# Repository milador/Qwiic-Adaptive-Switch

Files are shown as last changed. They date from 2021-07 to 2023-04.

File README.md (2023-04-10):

# Qwiic-Adaptive-Switch

Qwiic-Adaptive-Switch modules provide an easy way to create your own adaptive switch input or output boxes through Qwiic or STEMMA QT ecosystem. Qwiic Adaptive Switch modules can be connected to any Qwiic enabled board to create an adaptive switch box.

You can find more information about <a href="https://www.sparkfun.com/qwiic">Qwiic Connect System</a> at SparkFun official website.

Qwiic-Adaptive-Switch modules use Qwiic/JST-SH-4Pin connector and IC2 interface to communicate with main microcontroller which means you can connect multiple switch modules by daisy chaining them. It's using TCA9534 bus expander.

## Qwiic-Adaptive-Switch-Input

Top View: 
<p align="center">
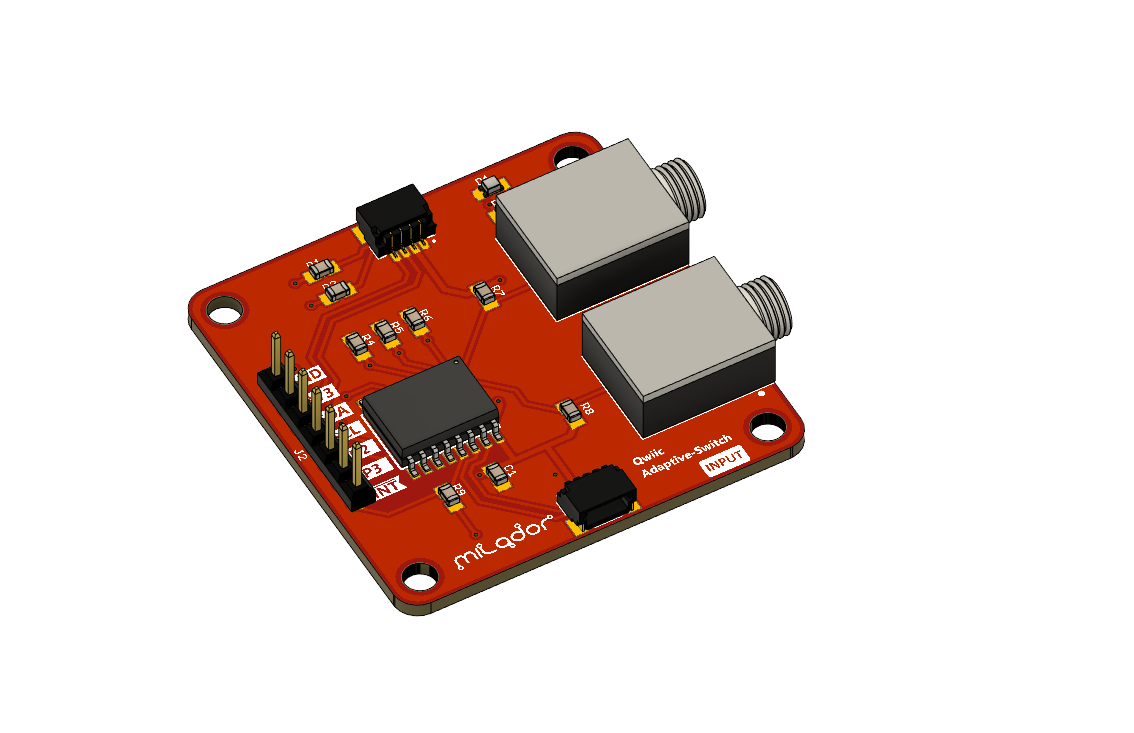
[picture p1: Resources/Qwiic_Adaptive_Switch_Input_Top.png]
Qwiic Adaptive Switch Input Top

</p>

Bottom View:
<p align="center">
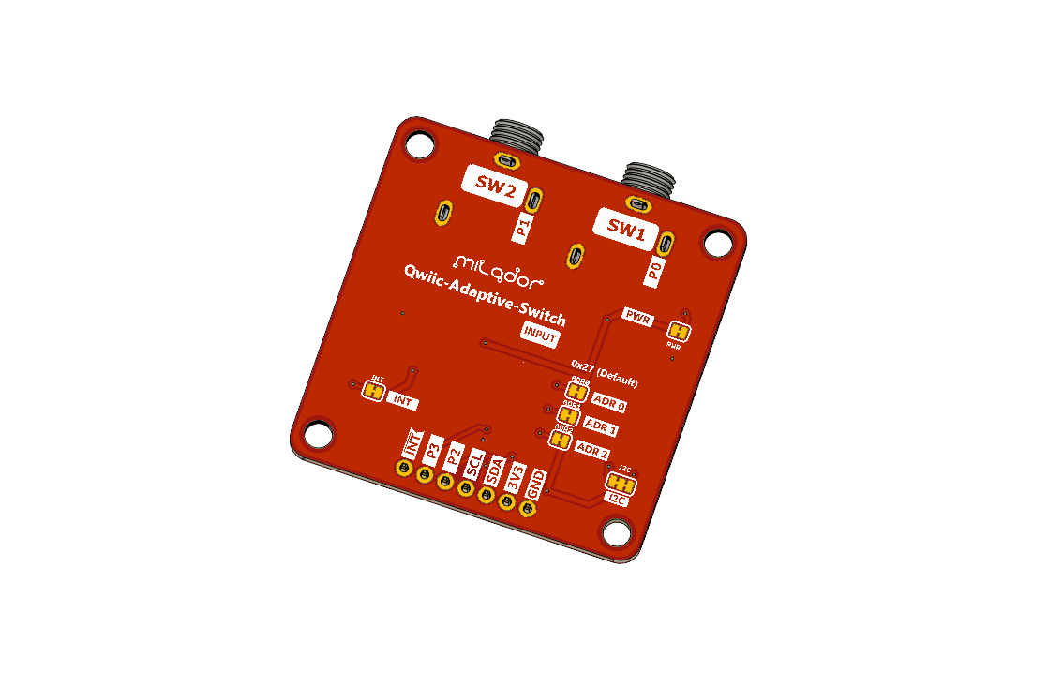
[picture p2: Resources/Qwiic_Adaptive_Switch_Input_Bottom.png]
Qwiic Adaptive Switch Input Bottom

</p>

## Qwiic-Adaptive-Switch-Output

Top View: 
<p align="center">
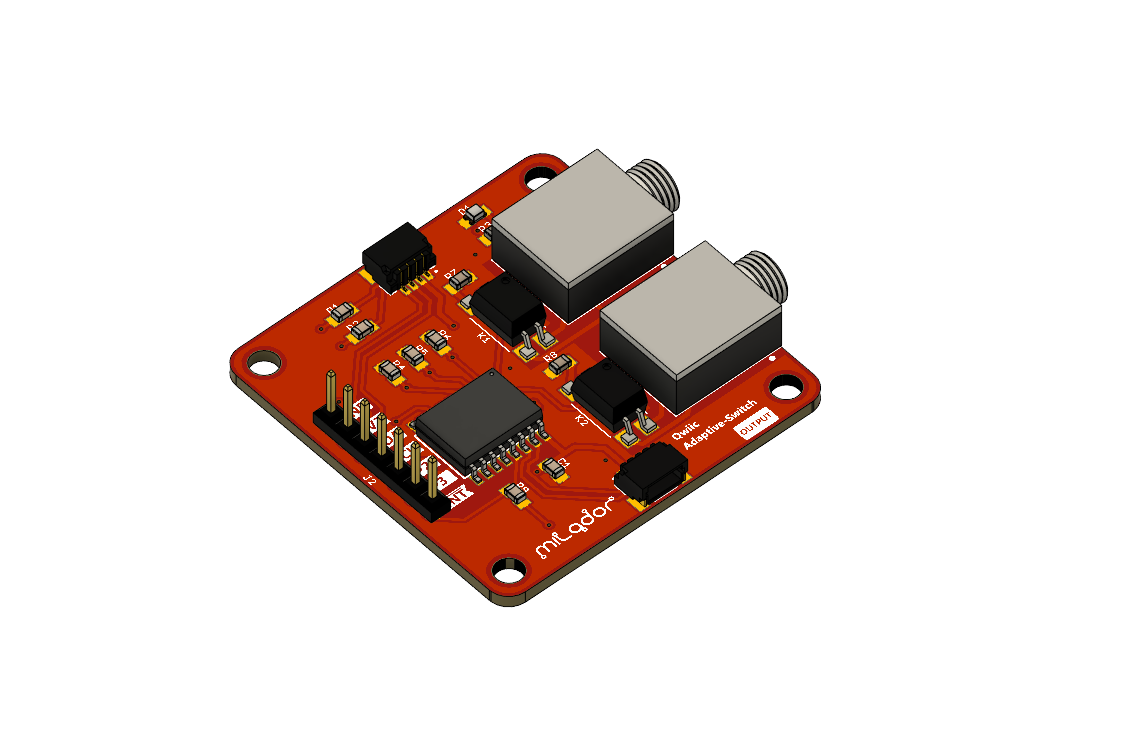
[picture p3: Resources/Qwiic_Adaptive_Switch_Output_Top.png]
Qwiic Adaptive Switch Output Top

</p>

Bottom View:
<p align="center">
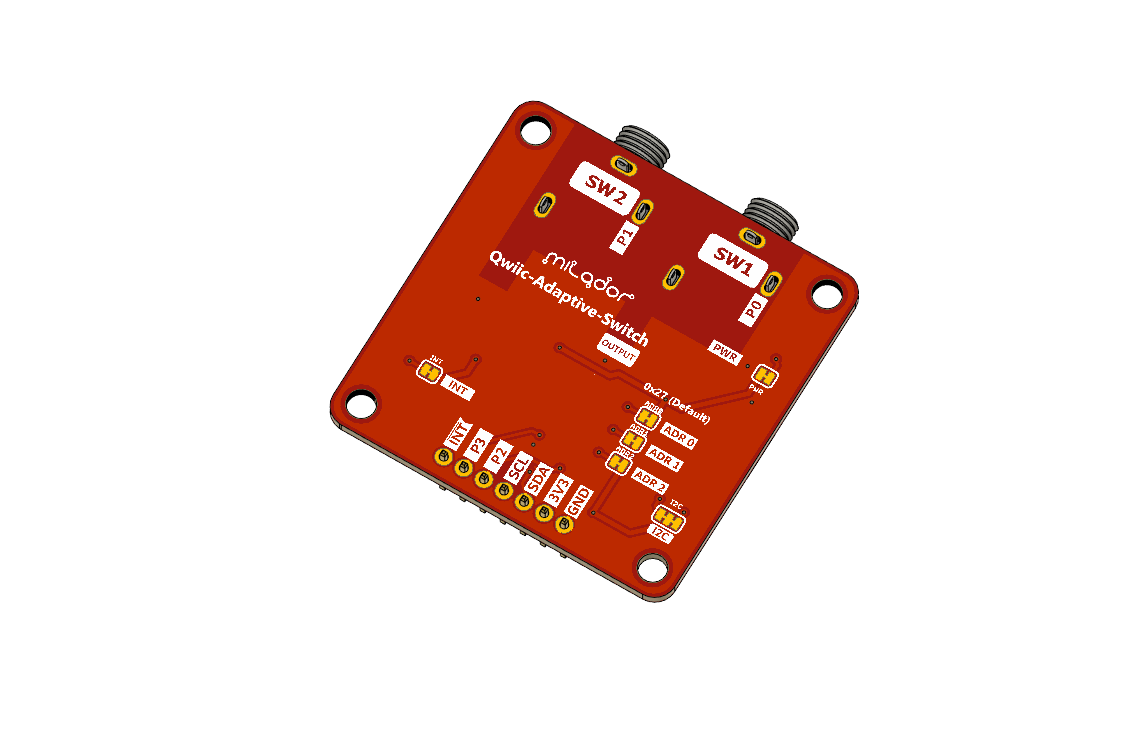
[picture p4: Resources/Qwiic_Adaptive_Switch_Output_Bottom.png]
Qwiic Adaptive Switch Output Bottom

</p>

## Risk Assessment

The Risk Assessment documents are located under [Documents](./Documents/) directory. 

## License

### MIT License

Copyright (c) 2021 milador

Permission is hereby granted, free of charge, to any person obtaining a copy of this software and associated documentation files (the "Software"), to deal in the Software without restriction, including without limitation the rights to use, copy, modify, merge, publish, distribute, sublicense, and/or sell copies of the Software, and to permit persons to whom the Software is furnished to do so, subject to the following conditions:

The above copyright notice and this permission notice shall be included in all copies or substantial portions of the Software.

THE SOFTWARE IS PROVIDED "AS IS", WITHOUT WARRANTY OF ANY KIND, EXPRESS OR IMPLIED, INCLUDING BUT NOT LIMITED TO THE WARRANTIES OF MERCHANTABILITY, FITNESS FOR A PARTICULAR PURPOSE AND NONINFRINGEMENT. IN NO EVENT SHALL THE AUTHORS OR COPYRIGHT HOLDERS BE LIABLE FOR ANY CLAIM, DAMAGES OR OTHER LIABILITY, WHETHER IN AN ACTION OF CONTRACT, TORT OR OTHERWISE, ARISING FROM, OUT OF OR IN CONNECTION WITH THE SOFTWARE OR THE USE OR OTHER DEALINGS IN THE SOFTWARE.

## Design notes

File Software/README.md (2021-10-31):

# Qwiic-Adaptive-Switch

## Software 

Qwiic-Adaptive-Switch-Input and Qwiic-Adaptive-Switch-Output modules both use TCA9534 bus expander to read or write status of switches. The TCA9534 bus expander converts GPIO to I2C data and you can use the existing I2C TCA9534 libraries to help you get started.

## Library 

### Arduino Library
You have two options if you are planning to use C++ and Arduino to write your code.

  1. [SparkFun_Qwiic_GPIO_Library](https://github.com/sparkfun/SparkFun_Qwiic_GPIO_Library) ( TCA9534 library created by SparkFun to be used with Qwiic Bus-Expander module )
  2. [TCA9534 library](https://github.com/hideakitai/TCA9534) ( TCA9534 library created by hideakitai )

### CircuitPython Library
You have the option to use the <a href="https://github.com/milador/Community_CircuitPython_TCA9534">Community_CircuitPython_TCA9534</a> library if you are planning to write your code in CircuitPython. 

## Example Code 

### Qwiic-Adaptive-Switch-Input Example Code

There is an example available to help you get started with Qwiic-Adaptive-Switch-Input module and SparkFun TCA9534 library. The <a href="https://raw.githubusercontent.com/milador/Qwiic-Adaptive-Switch/main/Software/Arduino/Qwiic_Adaptive_Switch_Input/Qwiic_Adaptive_Switch_Input.ino">Qwiic_Adaptive_Switch_Input.ino</a> example is available for testing purposes.

### Qwiic-Adaptive-Switch-Output Example Code

There is an example available to help you get started with Qwiic-Adaptive-Switch-Output module and SparkFun TCA9534 library. The <a href="https://raw.githubusercontent.com/milador/Qwiic-Adaptive-Switch/main/Software/Arduino/Qwiic_Adaptive_Switch_Output/Qwiic_Adaptive_Switch_Output.ino">Qwiic_Adaptive_Switch_Output.ino</a> example is available for testing purposes.

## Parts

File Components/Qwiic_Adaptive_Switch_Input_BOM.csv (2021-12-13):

Index | Quantity | Item | Value | Digikey Part Number | Manufacturer Part Number | Description | Unit Price (CAD) | Total Price (CAD) | Link
1 | 2 | SW1,SW2 | SJ1-3513 | CP1-3513-ND | SJ1-3513 | CONN JACK STEREO 3.5MM R/A | 1.97 | 1.97 | https://www.digikey.ca/en/products/detail/cui-devices/SJ1-3513/738683
2 | 1 | U1 | TCA9534DWR | 296-47827-1-ND | TCA9534DWR | IC I/O EXPANDER I2C 8B 16-SOIC | 1.82 | 1.82 | https://www.digikey.ca/en/products/detail/texas-instruments/TCA9534DWR/6566100
3 | 2 | J1,J3 | QWIIC JST | PRT-14417-ND | PRT-14417 | QWIIC JST CONNECTOR - SMD 4-PIN | 0.69 | 0.69 | https://www.digikey.ca/en/products/detail/sparkfun-electronics/PRT-14417/7652746
4 | 5 | R1,R2,R4,R5,R6 | 2.2K | 311-2.20KCRCT-ND | RC0805FR-072K2L | RES 2.2K OHM 1% 1/8W 0805 | 0.15 | 0.15 | https://www.digikey.ca/en/products/detail/yageo/RC0805FR-072K2L/727676
5 | 1 | R3 | 1K | 311-1.00KCRCT-ND | RC0805FR-071KL | RES 1K OHM 1% 1/8W 0805 | 0.15 | 0.15 | https://www.digikey.ca/en/products/detail/yageo/RC0805FR-071KL/727444
6 | 2 | R7,R8 | 4.7K | 311-4.7KARCT-ND | RC0805JR-074K7L | RES 4.7K OHM 5% 1/8W 0805 | 0.15 | 0.15 | https://www.digikey.ca/en/products/detail/yageo/RC0805JR-074K7L/728327
7 | 1 | R9 | 10K | 311-10.0KCRCT-ND | RC0805FR-0710KL | RES 10K OHM 1% 1/8W 0805 | 0.15 | 0.15 | https://www.digikey.ca/en/products/detail/yageo/RC0805FR-0710KL/727535
8 | 1 | C1 | 0.1 µF | 478-3755-1-ND | 08053C104KAT2A | CAP CER 0.1UF 25V X7R 0805 | 0.14 | 0.14 | https://www.digikey.ca/en/products/detail/avx-corporation/08053C104KAT2A/1116281
9 | 1 | LED (D1) | Red 631nm LED | 160-1436-2-ND | LTST-C190KRKT | LED RED CLEAR CHIP SMD | 0.33 | 0.33 | https://www.digikey.ca/en/products/detail/lite-on-inc/LTST-C190KRKT/386817
 |  |  |  |  |  |  | Total Price: | 8.96

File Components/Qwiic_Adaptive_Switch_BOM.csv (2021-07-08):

Index | Quantity | Item | Value | Digikey Part Number | Manufacturer Part Number | Description | Unit Price (C) | Total Price (CA) | Link
1 | 2 | SW1,SW2 | SJ1-3513 | CP1-3513-ND | SJ1-3513 | CONN JACK STEREO 3.5MM R/A | 1.97 | 1.97 | https://www.digikey.ca/en/products/detail/cui-devices/SJ1-3513/738683
2 | 1 | U1 | TCA9534DWR | 296-47827-1-ND | TCA9534DWR | IC I/O EXPANDER I2C 8B 16-SOIC | 1.82 | 1.82 | https://www.digikey.ca/en/products/detail/texas-instruments/TCA9534DWR/6566100
3 | 2 | J1,J3 | QWIIC JST | PRT-14417-ND | PRT-14417 | QWIIC JST CONNECTOR - SMD 4-PIN | 0.69 | 0.69 | https://www.digikey.ca/en/products/detail/sparkfun-electronics/PRT-14417/7652746
4 | 5 | R1,R2,R7,R8,R9 | 2.2K | 311-2.20KHRTR-ND | RC0603FR-072K2L | RES SMD 2.2K OHM 1% 1/10W 0603 | 0.15 | 0.15 | https://www.digikey.ca/en/products/detail/yageo/RC0603FR-072K2L/727016
5 | 1 | R3 | 10K | 311-10KGRTR-ND | RC0603JR-0710KL | RES SMD 10K OHM 5% 1/10W 0603 | 0.14 | 0.14 | https://www.digikey.ca/en/products/detail/yageo/RC0603JR-0710KL/726700
6 | 1 | R4 | 1K | 311-1.00KHRTR-ND | RC0603FR-071KL | RES SMD 1K OHM 5% 1/10W 0603 | 0.14 | 0.14 | https://www.digikey.ca/en/products/detail/yageo/RC0603FR-071KL/726843
7 | 2 | R5,R6 | 4.7K | 311-4.7KGRTR-ND | RC0603JR-074K7L | RES SMD 4.7K OHM 5% 1/10W 0603 | 0.25 | 0.14 | https://www.digikey.ca/en/products/detail/yageo/RC0603JR-074K7L/726785
8 | 1 | C1 | 0.1 µF | 587-1245-2-ND | TMK107BJ104KA-T | CAP CER 0.1UF 25V X5R 0603 | 0.14 | 0.14 | https://www.digikey.ca/en/products/detail/taiyo-yuden/TMK107BJ104KA-T/930597
9 | 1 | LED (D1) | Red 631nm LED | 160-1436-2-ND | LTST-C190KRKT | LED RED CLEAR CHIP SMD | 0.33 | 0.33 | https://www.digikey.ca/en/products/detail/lite-on-inc/LTST-C190KRKT/386817
 |  |  |  |  |  |  | Total Price: | 9.14

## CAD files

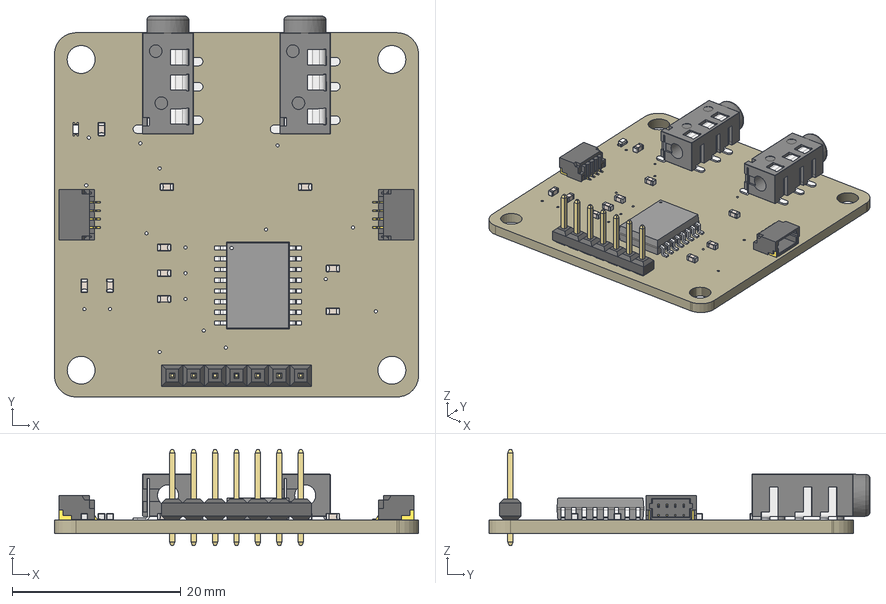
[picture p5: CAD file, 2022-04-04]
Hardware/3D-Model/Qwiic_Adaptive_Switch_Input_Assembly_RevA .step
43.2 x 45.2 x 11.4 mm
Board
Pin1 x 10
Pin2 x 10
CeramicBody x 10
CONNECTORS_JST04_1MM_RA x 2
PJ320A x 2
PJ320D-Pin x 6
PJ320D-Pin-B x 2
CONNECTORS_1X07_NO_SILK
LABEL-!INT x 2
LABEL-3V x 2
LABEL-ADDRESS-27
LABEL-ADR0
LABEL-ADR1
LABEL-ADR2
LABEL-GND x 2
LABEL-I2C
LABEL-INT
LABEL-P0
LABEL-P1
LABEL-P2 x 2
LABEL-P3 x 2
LABEL-PWR
LABEL-SCL x 2
LABEL-SDA x 2
MILADOR_LOGO1 x 2
MILADOR_QWIIC_SWITCH_SM
MILADOR_QWIIC_SWITCH
SWITCH-INPUT x 2
SWITCH-SW1
SWITCH-SW2

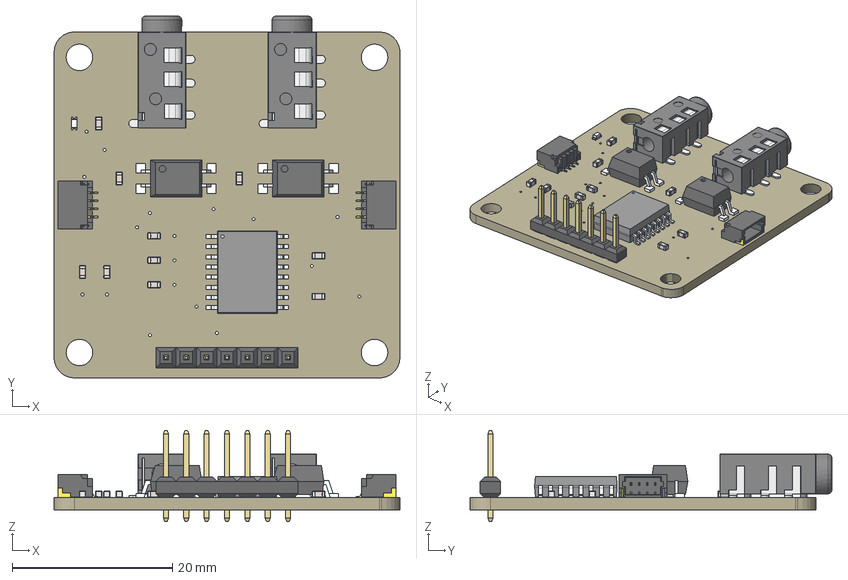
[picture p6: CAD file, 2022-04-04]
Hardware/3D-Model/Qwiic_Adaptive_Switch_Output_Assembly_RevA.step
43.2 x 45.2 x 11.4 mm
Board
Pin1 x 10
Pin2 x 10
CeramicBody x 10
CONNECTORS_JST04_1MM_RA x 2
G3VM-41DY1 x 2
PJ320A x 2
PJ320D-Pin x 6
PJ320D-Pin-B x 2
CONNECTORS_1X07_NO_SILK
LABEL-!INT x 2
LABEL-3V x 2
LABEL-ADDRESS-26
LABEL-ADR0
LABEL-ADR1
LABEL-ADR2
LABEL-GND x 2
LABEL-I2C
LABEL-INT
LABEL-P0
LABEL-P1
LABEL-P2 x 2
LABEL-P3 x 2
LABEL-PWR
LABEL-SCL x 2
LABEL-SDA x 2
MILADOR_LOGO1 x 2
MILADOR_QWIIC_SWITCH_SM
MILADOR_QWIIC_SWITCH
SWITCH-OUTPUT x 2
SWITCH-SW1
SWITCH-SW2

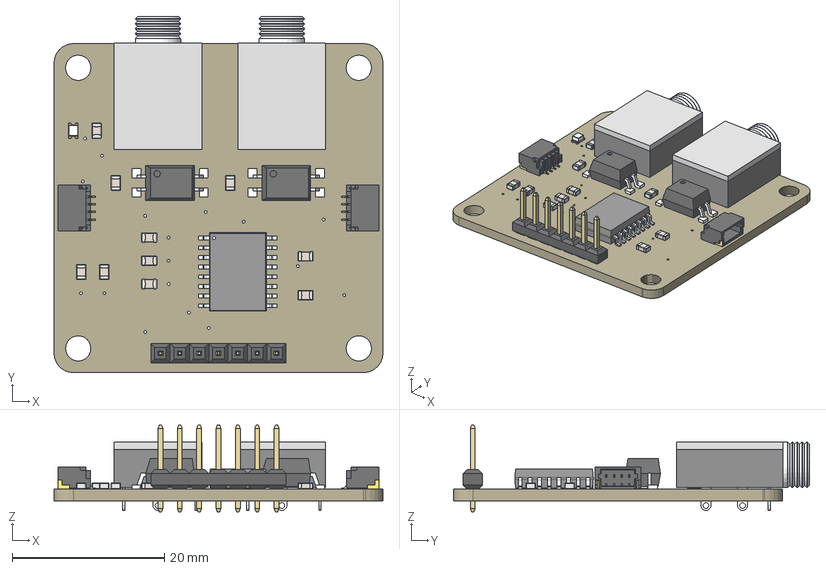
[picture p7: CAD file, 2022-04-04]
Hardware/3D-Model/Qwiic_Adaptive_Switch_Output.step
43.2 x 46.7 x 11.4 mm
Board
CUI_SJ1-3513 x 2
CONNECTORS_JST04_1MM_RA x 2
Pin1 (1) x 10
Pin2 (1) x 10
CeramicBody (1) x 10
G3VM-41DY1 x 2
CONNECTORS_1X07_NO_SILK
LABEL-!INT x 2
LABEL-3V x 2
LABEL-ADDRESS-27
LABEL-ADR0
LABEL-ADR1
LABEL-ADR2
LABEL-GND x 2
LABEL-I2C
LABEL-INT
LABEL-P0
LABEL-P1
LABEL-P2 x 2
LABEL-P3 x 2
LABEL-PWR
LABEL-SCL x 2
LABEL-SDA x 2
MILADOR_LOGO1 x 2
MILADOR_QWIIC_SWITCH_SM
MILADOR_QWIIC_SWITCH
SWITCH-OUTPUT x 2
SWITCH-SW1
SWITCH-SW2

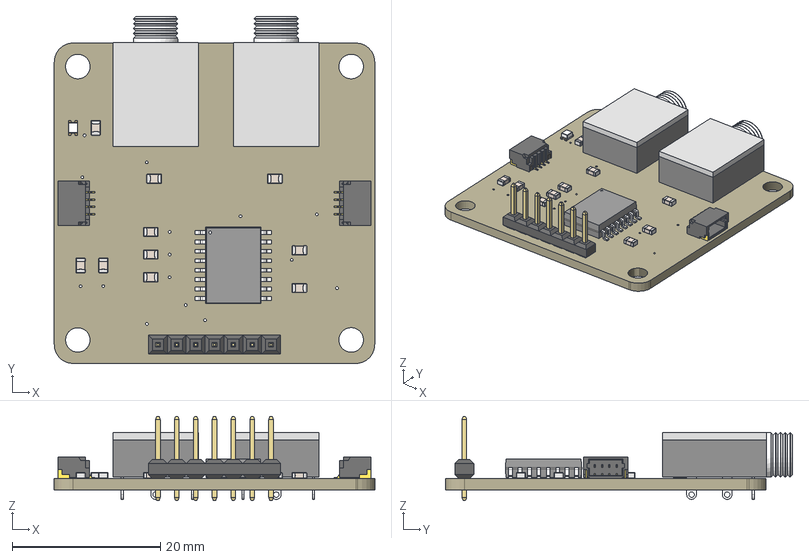
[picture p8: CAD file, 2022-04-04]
Hardware/3D-Model/Qwiic_Adaptive_Switch_Input.step
43.2 x 46.7 x 11.4 mm
Board
CUI_SJ1-3513 x 2
CONNECTORS_JST04_1MM_RA x 2
Pin1 (1) x 10
Pin2 (1) x 10
CeramicBody (1) x 10
CONNECTORS_1X07_NO_SILK
LABEL-!INT x 2
LABEL-3V x 2
LABEL-ADR0
LABEL-ADR1
LABEL-ADR2
LABEL-GND x 2
LABEL-I2C
LABEL-P0
LABEL-P1
LABEL-P2 x 2
LABEL-P3 x 2
LABEL-PWR
LABEL-SCL x 2
LABEL-SDA x 2
MILADOR_LOGO1 x 2
SWITCH-INPUT x 2
SWITCH-SW1
SWITCH-SW2
LABEL-ADDRESS-27
LABEL-INT
MILADOR_QWIIC_SWITCH_SM
MILADOR_QWIIC_SWITCH

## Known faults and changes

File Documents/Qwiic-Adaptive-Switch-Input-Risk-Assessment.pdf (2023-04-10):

## Product/Project Risk Assessment

Name/Title: | Qwiic-Adaptive-Switch
Description: | A module which provide an easy way to create your own adaptive switch input or output boxes through Qwiic or STEMMA QT ecosystem.
Assessment: | 2023-04-10
Developer: | Milador Technology Ltd.
Distributor: | Milador Technology Ltd.
Contact: | info@milador.ca
Link: | www.milador.ca

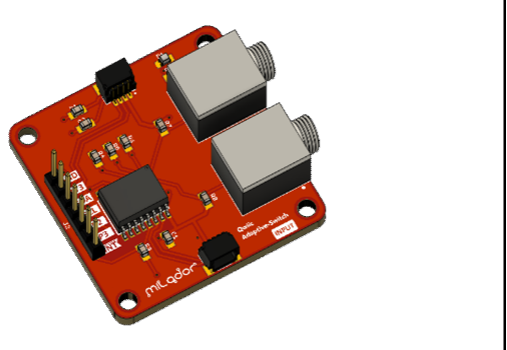
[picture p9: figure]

Assessment Summary: | The module provides minimum risk when it is used to create AT devices. It needs to be noted that module should not be used to create devices for emergency usage.
| Very Likely (3) | Possible (2) | Unlikely (1)
Major Injury (3) | (9) | (6) | (3)
Minor Injury (2) | (6) | (4) | (2)
Trival (1) | (3) | (2) | (1)

Identified Risks

ID | Name | Likelihood | Severity | Risk Level | Likelihood | Severity | Risk Level | Notes
1 | Dev board is damaged by short | 1 | 1 | 1 | 1 | 1 | 1 | Dev board can be replaced, check if dev board has fuse
2 | Computer is damaged | 1 | 1 | 1 | 1 | 1 | 1 | Most computers have fuse and reset button
3 | Fire risk from Qwiic connector | 1 | 2 | 2 | 1 | 2 | 2 | It's powered through Qwiic cable
4 | Qwiic and 3.5mm cable strangulation | 1 | 3 | 3 | 1 | 3 | 3 | Qwiic cable is 200mm at most
5 | Cutting risk if PCB is damaged | 1 | 2 | 2 | 1 | 2 | 2 | Make sure all corners are rounded
6 | Emergency Communication Failure | 2 | 3 | 6 | 2 | 3 | 6 | Must warn that the module should not be used to create devices for emergency usage
7 | None- Emergency Communication Failure | 2 | 1 | 2 | 2 | 1 | 2 | Normal risk of AT devices
8 | Installation Risk | 1 | 1 | 1 | 1 | 1 | 1 | The installation process should not require power tools

Mitigated

Mitigated Assessment | Likelihood Severity Severity

Initial

Initial Assessment | Likelihood
| | Very Likely (3) | Possible (2) | Unlikely (1)
| Major Injury (3) | (9) | (6) | (3)
| Minor Injury (2) | (6) | (4) | (2)
| Trival (1) | (3) | (2) | (1)

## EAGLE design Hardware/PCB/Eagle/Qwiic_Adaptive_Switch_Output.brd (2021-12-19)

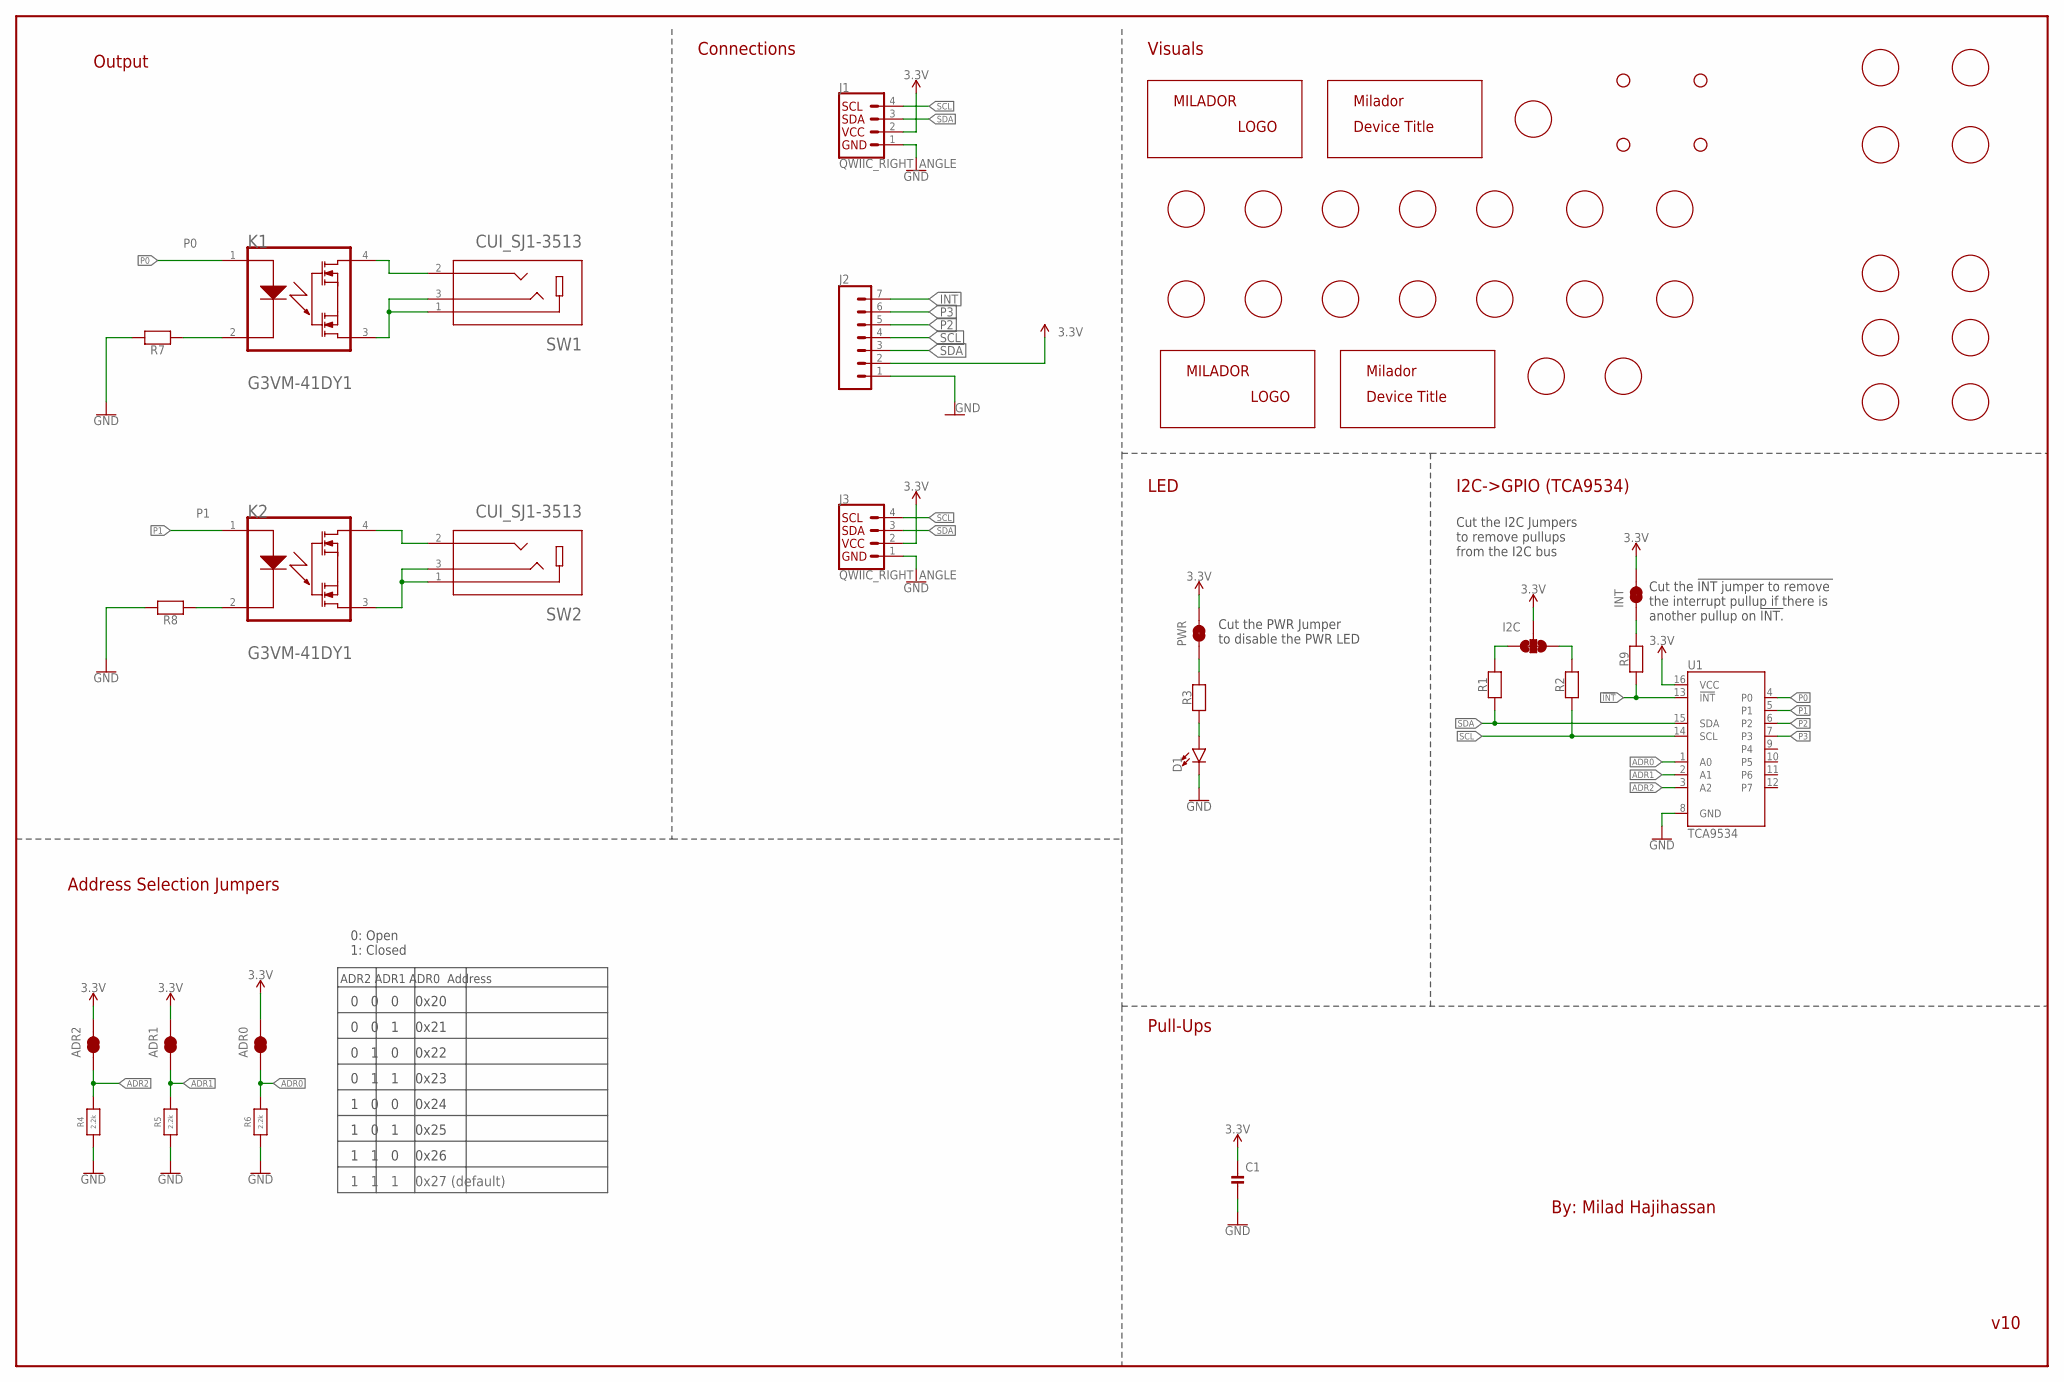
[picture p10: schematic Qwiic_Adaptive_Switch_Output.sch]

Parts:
ADR0, ADR1, ADR2: JUMPERS-SMT_2_NC_TRACE_SILK; JUMPERS_SMT-JUMPER_2_NC_TRACE_SILK
C1: 0.1uF; 0805-MP
D1: RED; CHIPLED_0805_NOOUTLINE
H1, H2, H3, H4: STAND-OFF-3.3
I2C: JUMPERS_JUMPER-SMT_3_2-NC_TRACE_SILK; JUMPERS_SMT-JUMPER_3_2-NC_TRACE_SILK
INT: JUMPERS-SMT_2_NC_TRACE_SILK; JUMPERS_SMT-JUMPER_2_NC_TRACE_SILK
J1, J3: QWIIC_RIGHT_ANGLE; CONNECTORS_JST04_1MM_RA
J2: CONNECTORS_CONN_071X07_NO_SILK; CONNECTORS_1X07_NO_SILK
K1, K2: G3VM-41DY1
LABEL_3V_BOTTOM, LABEL_3V_TOP: MILADOR-LABEL-3V; LABEL-3V
LABEL_!INT_BOTTOM: MILADOR-LABEL-!INT; LABEL-!INT
LABEL_!INT_TOP: MILADOR-LABEL-!INT; LABEL-!INT
LABEL_ADR0: MILADOR-LABEL-ADR0; LABEL-ADR0
LABEL_ADR1: MILADOR-LABEL-ADR1; LABEL-ADR1
LABEL_ADR2: MILADOR-LABEL-ADR2; LABEL-ADR2
LABEL_GND_BOTTOM: MILADOR-LABEL-GND; LABEL-GND
LABEL_GND_TOP: MILADOR-LABEL-GND; LABEL-GND
LABEL_I2C: MILADOR-LABEL-I2C; LABEL-I2C
LABEL_I2C_ADDRESS: MILADOR-LABEL-ADDRESS-0X27; LABEL-ADDRESS-27
LABEL_INT: MILADOR-LABEL-INT; LABEL-INT
LABEL_MILADOR_BOTTOM: MILADOR-LOGO-; MILADOR_LOGO1
LABEL_MILADOR_TOP: MILADOR-LOGO-; MILADOR_LOGO1
LABEL_OUTPUT_BOTTOM: MILADOR-SWITCH-NAME-SW-OUTPUT; SWITCH-OUTPUT
LABEL_OUTPUT_TOP: MILADOR-SWITCH-NAME-SW-OUTPUT; SWITCH-OUTPUT
LABEL_P0_BOTTOM: MILADOR-LABEL-P0; LABEL-P0
LABEL_P1_BOTTOM: MILADOR-LABEL-P1; LABEL-P1
LABEL_P2_BOTTOM, LABEL_P2_TOP: MILADOR-LABEL-P2; LABEL-P2
LABEL_P3_BOTTOM, LABEL_P3_TOP: MILADOR-LABEL-P3; LABEL-P3
LABEL_PWR: MILADOR-LABEL-PWR; LABEL-PWR
LABEL_SW1: MILADOR-SWITCH-NAME-SW1; SWITCH-SW1
LABEL_SW2: MILADOR-SWITCH-NAME-SW2; SWITCH-SW2
LABEL_TITLE_BOTTOM: MILADOR-DEVICE-QWIIC-SWITCH; MILADOR_QWIIC_SWITCH
LABEL_TITLE_TOP: MILADOR-DEVICE-QWIIC-SWITCH-SM; MILADOR_QWIIC_SWITCH_SM
LABE_SCL_BOTTOM: MILADOR-LABEL-SCL; LABEL-SCL
LABE_SCL_TOP: MILADOR-LABEL-SCL; LABEL-SCL
LABE_SDA_BOTTOM: MILADOR-LABEL-SDA; LABEL-SDA
LABE_SDA_TOP: MILADOR-LABEL-SDA; LABEL-SDA
PWR: JUMPERS-SMT_2_NC_TRACE_SILK; JUMPERS_SMT-JUMPER_2_NC_TRACE_SILK
R1, R2, R4, R5, R6: 2.2k; 0805-MP
R3: 1k; 0805-MP
R7, R8: 220; 0805-MP
R9: 10k; 0805-MP
SW1, SW2: CUI_SJ1-3513
U1: TCA9534; 16SOIC

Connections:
3.3V: ADR0.2, ADR1.2, ADR2.2, C1.1, I2C.2, INT.2, J1.2, J2.2, J3.2, PWR.2, U1.16 (VCC)
!INT: J2.7, R9.1, U1.13 (!INT)
ADR0: ADR0.1, R6.2, U1.1 (A0)
ADR1: ADR1.1, R5.2, U1.2 (A1)
ADR2: ADR2.1, R4.2, U1.3 (A2)
GND: C1.2, D1.C, J1.1, J2.1, J3.1, R4.1, R5.1, R6.1, R7.2, R8.2, U1.8 (GND)
unnamed: INT.1, R9.2
unnamed: D1.A, R3.1
unnamed: PWR.1, R3.2
unnamed: K1.4, SW1.2
unnamed: K1.2, R7.1
unnamed: K1.3, SW1.1, SW1.3
unnamed: K2.2, R8.1
unnamed: K2.4, SW2.2
unnamed: K2.3, SW2.1, SW2.3
P0: K1.1, U1.4 (P0)
P1: K2.1, U1.5 (P1)
P2: J2.5, U1.6 (P2)
P3: J2.6, U1.7 (P3)
SCL: J1.4, J2.4, J3.4, R2.1, U1.14 (SCL)
SCL_PU1: I2C.1, R1.2
SDA: J1.3, J2.3, J3.3, R1.1, U1.15 (SDA)
SDA_PU1: I2C.3, R2.2

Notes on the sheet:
v10
Address Selection Jumpers
ADR2 ADR1 ADR0 Address
0 0 0 0x20
0 0 1 0x21
0 1 0 0x22
0 1 1 0x23
1 0 0 0x24
1 0 1 0x25
1 1 0 0x26
1 1 1 0x27 (default)
0: Open 1: Closed
I2C->GPIO (TCA9534)
Connections
By: Milad Hajihassan
Cut the !INT jumper to remove the interrupt pullup if there is another pullup on !INT.
Cut the I2C Jumpers to remove pullups from the I2C bus
Cut the PWR Jumper to disable the PWR LED
LED
Visuals
Pull-Ups
Output

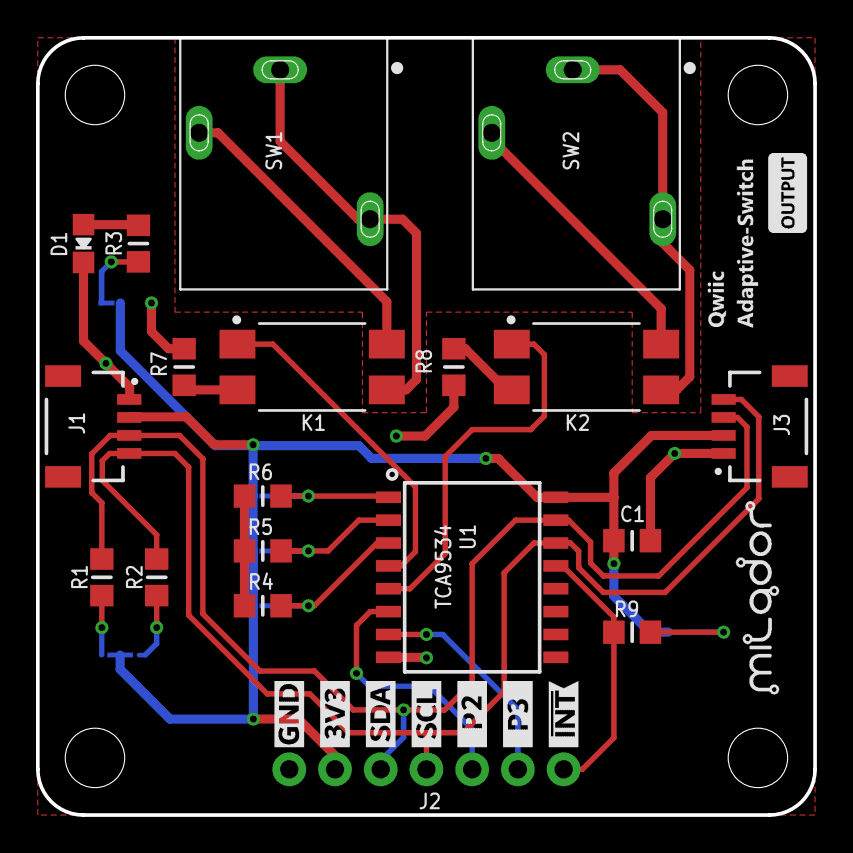
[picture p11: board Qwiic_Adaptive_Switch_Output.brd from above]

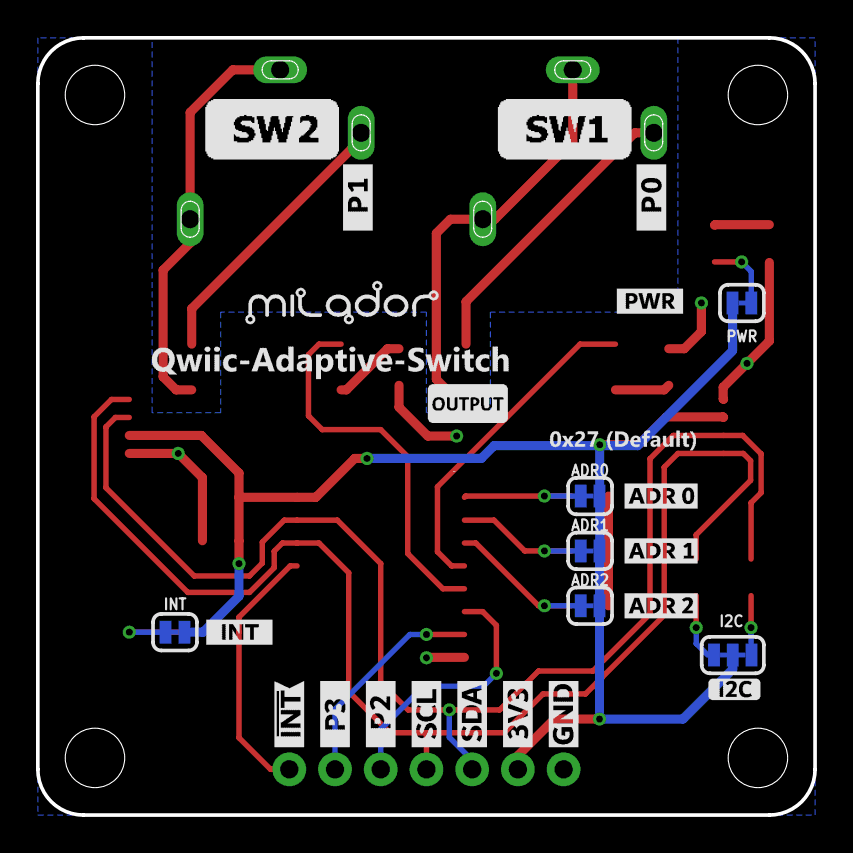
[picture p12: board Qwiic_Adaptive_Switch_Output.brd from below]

Board: 2 copper layers, 43.2 x 43.2 mm, 60 parts (27 on the bottom side), 23 nets.

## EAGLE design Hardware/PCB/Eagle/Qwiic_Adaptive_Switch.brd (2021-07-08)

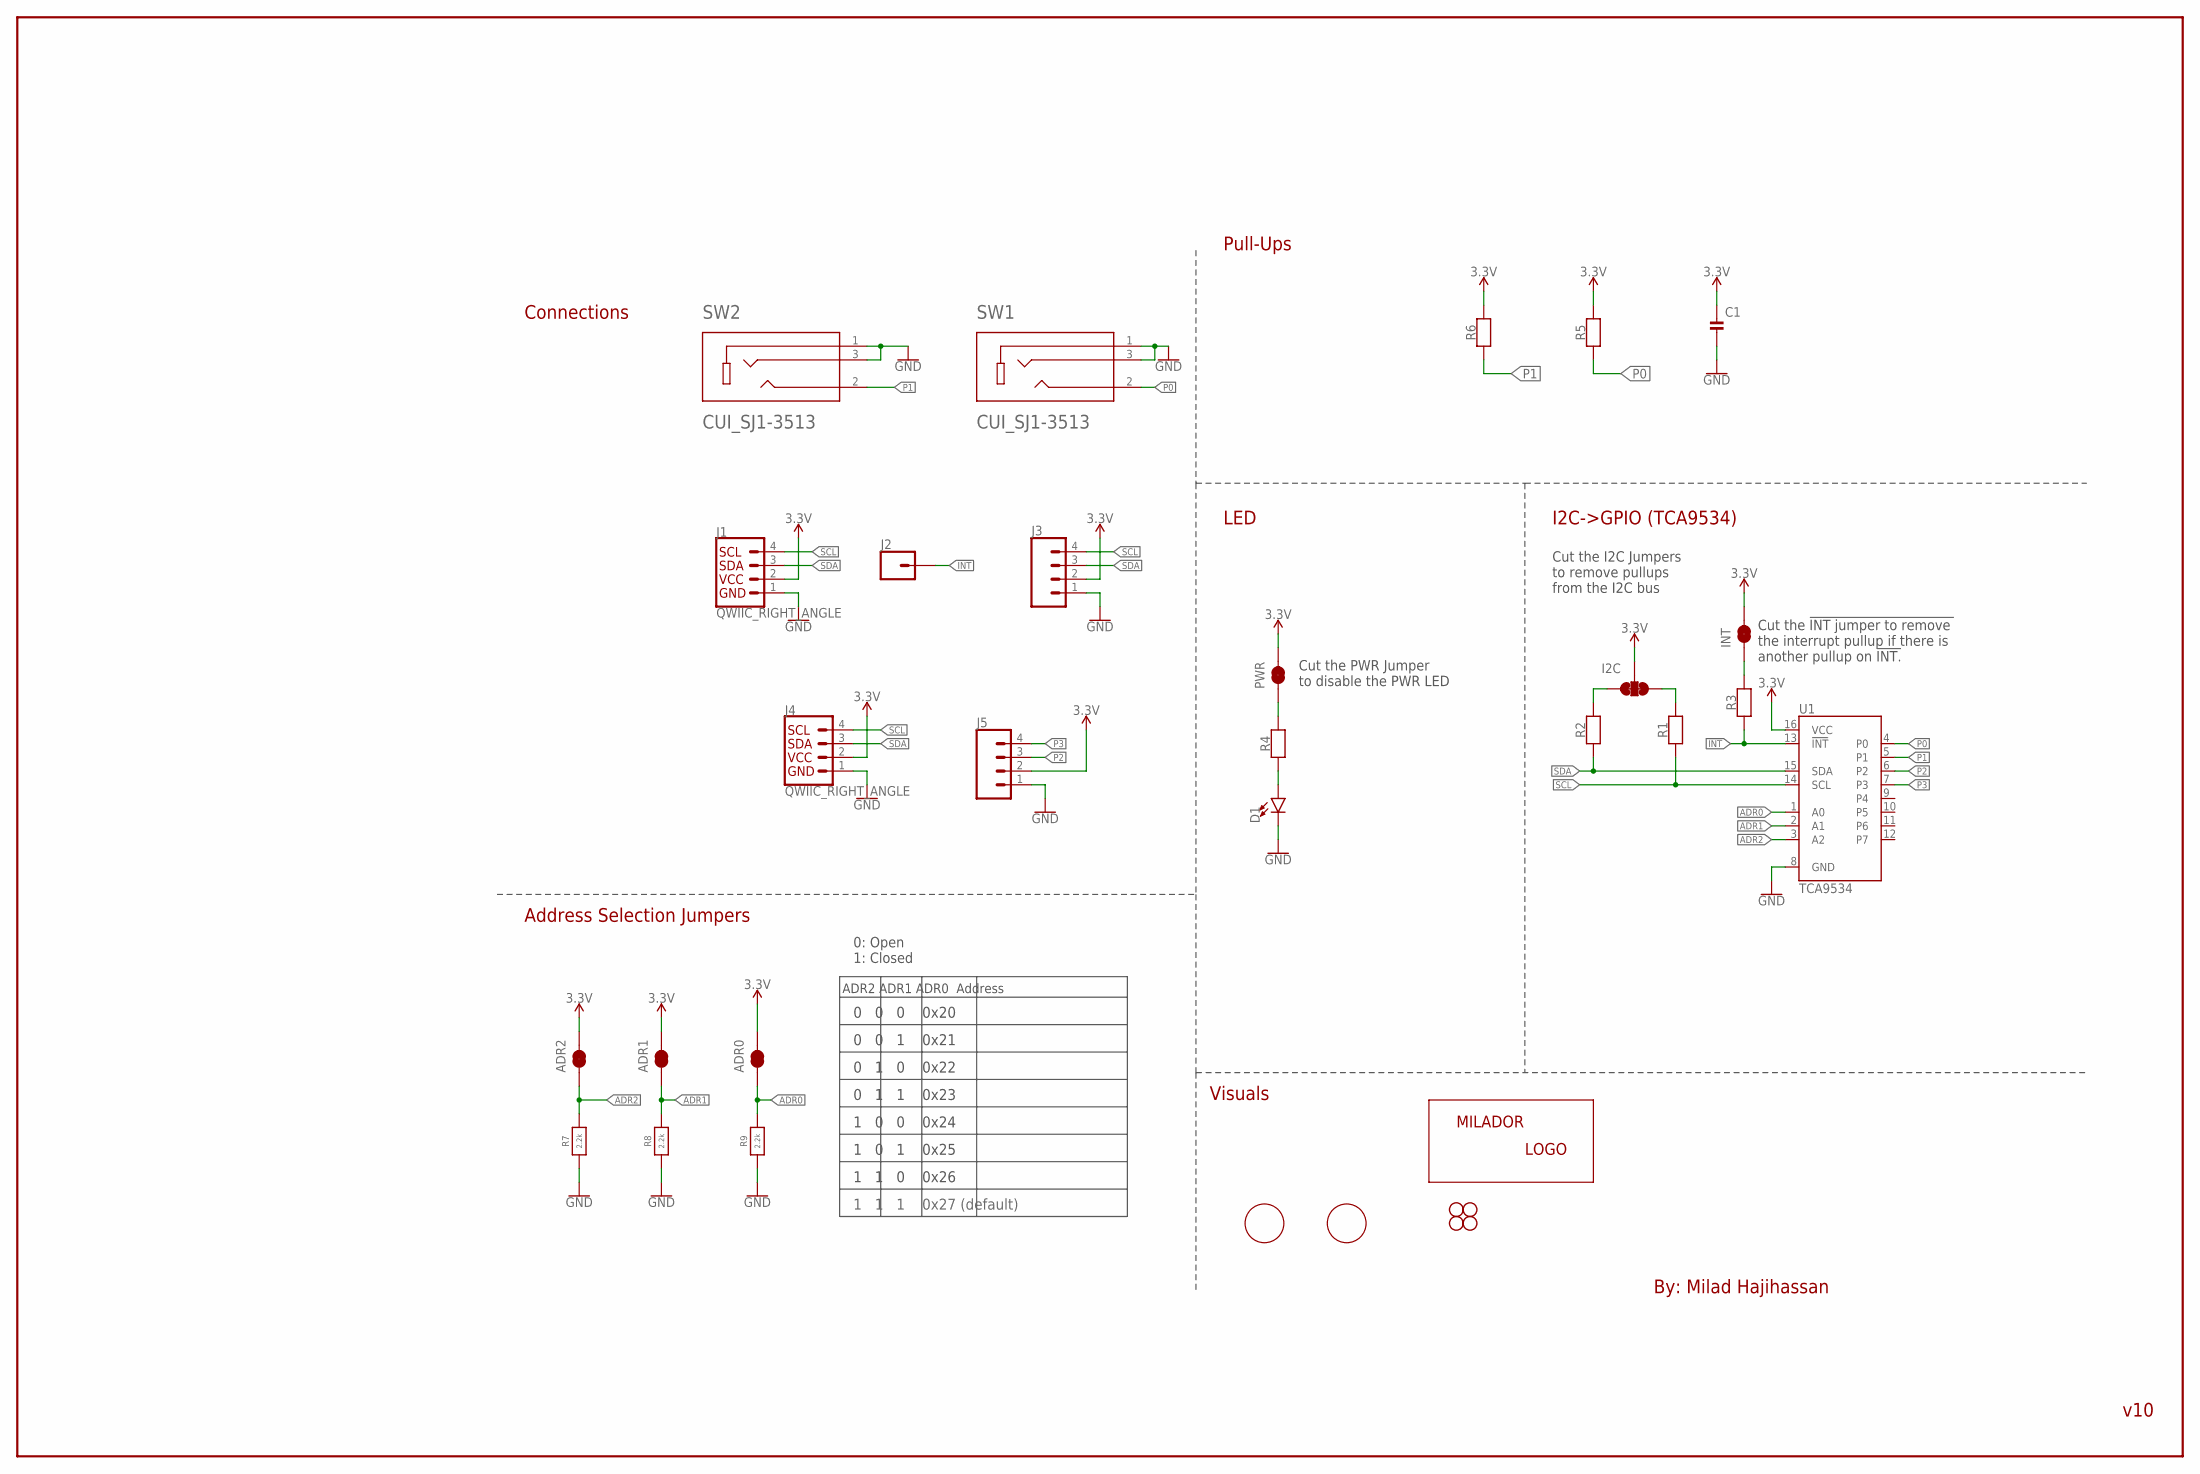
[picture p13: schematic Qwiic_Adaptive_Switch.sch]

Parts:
ADR0, ADR1, ADR2: JUMPERS-SMT_2_NC_TRACE_SILK; JUMPERS_SMT-JUMPER_2_NC_TRACE_SILK
C1: 0.1uF; 0603
D1: RED; LED-0603
H1, H2: STAND-OFF
I2C: JUMPERS_JUMPER-SMT_3_2-NC_TRACE_SILK; JUMPERS_SMT-JUMPER_3_2-NC_TRACE_SILK
INT: JUMPERS-SMT_2_NC_TRACE_SILK; JUMPERS_SMT-JUMPER_2_NC_TRACE_SILK
J1, J4: QWIIC_RIGHT_ANGLE; CONNECTORS_JST04_1MM_RA
J2: CONNECTORS_CONN_01PTH_NO_SILK_YES_STOP; CONNECTORS_1X01_NO_SILK
J3, J5: CONNECTORS_CONN_041X04_NO_SILK; CONNECTORS_1X04_NO_SILK
JP3, JP4: STAND-OFF
PWR: JUMPERS-SMT_2_NC_TRACE_SILK; JUMPERS_SMT-JUMPER_2_NC_TRACE_SILK
R1, R2, R7, R8, R9: 2.2k; 0603
R3, R5: 10k; 0603
R4: 1k; 0603
R6: 10K; 0603
SW1, SW2: CUI_SJ1-3513
U1: TCA9534; 16SOIC
U$6: MILADOR-LOGO-; MILADOR_LOGO1
U$17: MILADOR-SWITCH-NAME-SW1; SWITCH-SW1
U$18: MILADOR-SWITCH-NAME-SW2; SWITCH-SW2

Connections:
3.3V: ADR0.2, ADR1.2, ADR2.2, C1.1, I2C.2, INT.2, J1.2, J3.2, J4.2, J5.2, PWR.2, R5.2, R6.2, U1.16 (VCC)
!INT: J2.1, R3.1, U1.13 (!INT)
ADR0: ADR0.1, R9.2, U1.1 (A0)
ADR1: ADR1.1, R8.2, U1.2 (A1)
ADR2: ADR2.1, R7.2, U1.3 (A2)
GND: C1.2, D1.C, J1.1, J3.1, J4.1, J5.1, R7.1, R8.1, R9.1, SW1.1, SW1.3, SW2.1, SW2.3, U1.8 (GND)
unnamed: INT.1, R3.2
unnamed: D1.A, R4.1
unnamed: PWR.1, R4.2
P0: R5.1, SW1.2, U1.4 (P0)
P1: R6.1, SW2.2, U1.5 (P1)
P2: J5.3, U1.6 (P2)
P3: J5.4, U1.7 (P3)
SCL: J1.4, J3.4, J4.4, R1.1, U1.14 (SCL)
SCL_PU1: I2C.1, R2.2
SDA: J1.3, J3.3, J4.3, R2.1, U1.15 (SDA)
SDA_PU1: I2C.3, R1.2

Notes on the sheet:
v10
Address Selection Jumpers
ADR2 ADR1 ADR0 Address
0 0 0 0x20
0 0 1 0x21
0 1 0 0x22
0 1 1 0x23
1 0 0 0x24
1 0 1 0x25
1 1 0 0x26
1 1 1 0x27 (default)
0: Open 1: Closed
I2C->GPIO (TCA9534)
Connections
By: Milad Hajihassan
Cut the !INT jumper to remove the interrupt pullup if there is another pullup on !INT.
Cut the I2C Jumpers to remove pullups from the I2C bus
Cut the PWR Jumper to disable the PWR LED
LED
Visuals
Pull-Ups

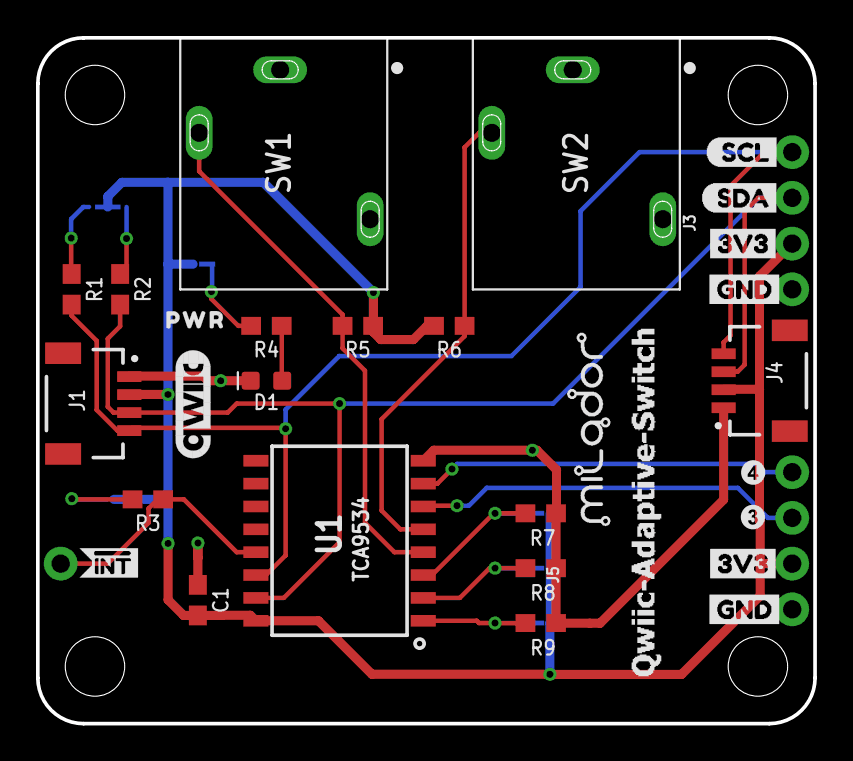
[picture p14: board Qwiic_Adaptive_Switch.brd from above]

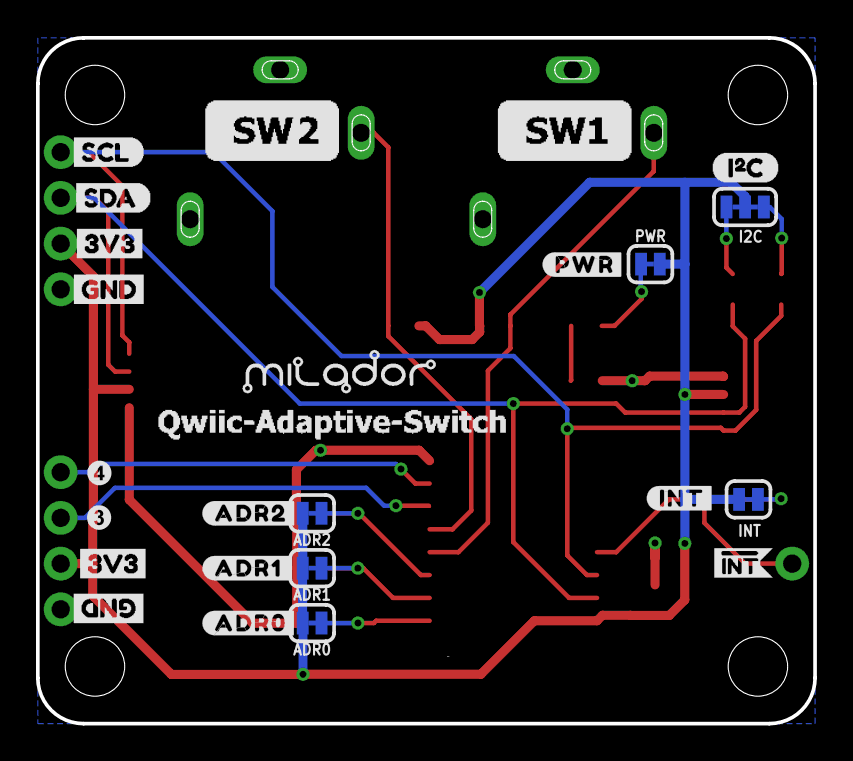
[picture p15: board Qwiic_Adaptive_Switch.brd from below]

Board: 2 copper layers, 43.2 x 38.1 mm, 57 parts (23 on the bottom side), 17 nets.

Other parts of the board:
U$1: I2C
U$2, U$7, U$14, U$25: GND4
U$3, U$4, U$8, U$26: 3V33
U$5: #ADR1#0
U$9: SCL6
U$10: SDA5
U$11: #ADR2#0
U$12: #INT#0
U$13, U$22: #INT0
U$15: #ADR0#0
U$16, U$19: MILADOR_QWIIC_SWITCH
U$20: MILADOR-LOGO-; MILADOR_LOGO1
U$21: QWIIC_6MM
U$23: SCL0
U$24: SDA1
U$34: PWR0
U$39: #PWR#0

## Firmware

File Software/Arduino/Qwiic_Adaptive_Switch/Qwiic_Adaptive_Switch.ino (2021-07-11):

/******************************************************************************
  Title: Qwiic Adaptive Switch Example
  File: Qwiic_Adaptive_Switch.ino
  Created: July 10, 2021
  https://github.com/milador/Qwiic-Adaptive-Switch

  This is an example that allows the user to read the status of all 2 switches simultaneously

******************************************************************************/

#include <Wire.h>
#include "SparkFun_TCA9534.h"

TCA9534 myGPIO;

#define NUM_GPIO 4

bool currentPinMode[NUM_GPIO] = {GPIO_IN, GPIO_IN, GPIO_IN, GPIO_IN};

bool gpioStatus[NUM_GPIO];

void setup() {
  Serial.begin(115200);
  Serial.println("Qwiic Adaptive Switch Example");
  Wire.begin();
  if (myGPIO.begin() == false) {
    Serial.println("Check Connections. No Qwiic GPIO detected.");
    while (1);
  }

  myGPIO.pinMode(currentPinMode);
}

void loop() {

  Serial.print("Switch array: ");
  for (uint8_t arrayPosition = 0; arrayPosition < NUM_GPIO; arrayPosition++) {
    gpioStatus[arrayPosition] = myGPIO.digitalRead(arrayPosition);
    switch (gpioStatus[arrayPosition])
    {
      case true:
        Serial.print("HIGH");
        break;
      case false:
        Serial.print("LOW");
        break;
    }
    if(arrayPosition<NUM_GPIO-1){
      Serial.print(",");
    }
  }
  Serial.println("\n");
  delay(100);
}

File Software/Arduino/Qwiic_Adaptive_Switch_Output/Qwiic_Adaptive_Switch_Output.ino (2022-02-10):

/******************************************************************************
  Title: Qwiic Adaptive Switch Output Example
  File: Qwiic_Adaptive_Switch_Output.ino
  Created: October 30, 2021
  https://github.com/milador/Qwiic-Adaptive-Switch

  This is an example that allows the user to output the status of all 2 switches simultaneously

******************************************************************************/

#include <Wire.h>
#include "SparkFun_TCA9534.h"


#define IC_ADDR              0x26
#define NUM_GPIO 4
TCA9534 myGPIO;

bool currentPinMode[NUM_GPIO] = {GPIO_OUT, GPIO_OUT, GPIO_OUT, GPIO_OUT};

bool gpioStatus[NUM_GPIO];

void setup() {
  Serial.begin(115200);
  Serial.println("Qwiic Adaptive Switch Output Example");
  Wire.begin();
  if (myGPIO.begin(Wire,IC_ADDR) == false) {
    Serial.println("Check Connections. No Qwiic GPIO detected.");
    while (1);
  }

  myGPIO.pinMode(currentPinMode);
}

void loop() {

  Serial.print("Switch array: ");
  for (uint8_t arrayPosition = 0; arrayPosition < NUM_GPIO; arrayPosition++) {
    myGPIO.digitalWrite(arrayPosition, HIGH);
    Serial.print("GPIO");
    Serial.print(arrayPosition);
    Serial.print(":");
    Serial.println("HIGH");
    delay(1000);
    myGPIO.digitalWrite(arrayPosition, LOW);
    Serial.print("GPIO");
    Serial.print(arrayPosition);
    Serial.print(":");
    Serial.println("LOW");          
    delay(1000);
  }
  delay(100);
}

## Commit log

2021-01-07 Added BOM file
    [Qwiic_Adaptive_Switch_BOM.csv, Qwiic_Adaptive_Switch_BOM.xlsx]
2021-01-07 Added Eagle PCB Design files
    [Qwiic_Adaptive_Switch.brd, Qwiic_Adaptive_Switch.sch]
2021-01-07 Added Gerber files
    [Qwiic_Adaptive_Switch.GBL, Qwiic_Adaptive_Switch.GBO, Qwiic_Adaptive_Switch.GBP, Qwiic_Adaptive_Switch.GBS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]
2021-01-07 Updated BOM File
    [Qwiic_Adaptive_Switch_BOM.csv, Qwiic_Adaptive_Switch_BOM.xlsx]
2021-01-08 Updated part list
    [Qwiic_Adaptive_Switch_BOM.csv, Qwiic_Adaptive_Switch_BOM.xlsx]
2021-01-09 Added Single and I2C BOM files
    [Qwiic_Adaptive_Switch.GBL, Qwiic_Adaptive_Switch.GBO, Qwiic_Adaptive_Switch.GBP, Qwiic_Adaptive_Switch.GBS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]
2021-01-09 Update silkscreen
    [Qwiic_Adaptive_Switch_Single.brd]
2021-01-09 Added pictures of PCB 3D model
2021-04-21 Updated BOM
    [Qwiic_Adaptive_Switch_BOM.csv, Qwiic_Adaptive_Switch_BOM.xlsx]
2021-05-30 Updated design
    [Qwiic_Adaptive_Switch.GBL, Qwiic_Adaptive_Switch.GBO, Qwiic_Adaptive_Switch.GBP, Qwiic_Adaptive_Switch.GBS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]
2021-06-05 Updated the design.
    [Qwiic_Adaptive_Switch.brd, Qwiic_Adaptive_Switch.sch, Qwiic_Adaptive_Switch_BOM.xlsx, Qwiic_Adaptive_Switch_Single.GBL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]
2021-07-08 Updated the design - Stable design
    [Qwiic_Adaptive_Switch.brd, Qwiic_Adaptive_Switch.sch, Qwiic_Adaptive_Switch_BOM.csv, Qwiic_Adaptive_Switch_BOM.xlsx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]
2021-07-11 Added Arduino example
2021-09-05 Renamed the module
    [Qwiic_Adaptive_Switch_BOM.xlsx, Qwiic_Adaptive_Switch_Input.brd, Qwiic_Adaptive_Switch_Input.sch, Qwiic_Adaptive_Switch_Input_BOM.csv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]
2021-09-05 Updated PCB
    [Qwiic_Adaptive_Switch_Input.brd]
2021-09-07 Added Switch Output
    [Qwiic_Adaptive_Switch_Input_BOM.xlsx, Qwiic_Adaptive_Switch_Output.brd, Qwiic_Adaptive_Switch_Output.sch, Qwiic_Adaptive_Switch_Output_BOM.csv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]
2021-09-07 Updated PCB Designs to match input with output designs
    [Qwiic_Adaptive_Switch_Input.brd, Qwiic_Adaptive_Switch_Output.brd]
2021-09-11 Updated PCB Mount holes
    [Qwiic_Adaptive_Switch_Input.brd, Qwiic_Adaptive_Switch_Input.sch, Qwiic_Adaptive_Switch_Output.brd, Qwiic_Adaptive_Switch_Output.sch]
2021-09-14 Updated footprints to 0805 packages
    [Qwiic_Adaptive_Switch_Input.brd, Qwiic_Adaptive_Switch_Input.sch, Qwiic_Adaptive_Switch_Input_BOM.csv, Qwiic_Adaptive_Switch_Input_BOM.xlsx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]
2021-09-18 Updated silkscreen
    [Qwiic_Adaptive_Switch_Input.brd, Qwiic_Adaptive_Switch_Input.sch, Qwiic_Adaptive_Switch_Output.brd, Qwiic_Adaptive_Switch_Output.sch]
2021-10-31 Added sample output code
2021-12-13 Updated design to version 1.2
    [Qwiic_Adaptive_Switch_Input.brd, Qwiic_Adaptive_Switch_Input.sch, Qwiic_Adaptive_Switch_Output.brd, Qwiic_Adaptive_Switch_Output.sch]
2021-12-13 Updated version 2.1 BOM
    [Qwiic_Adaptive_Switch_Input_BOM.csv, Qwiic_Adaptive_Switch_Input_BOM.xlsx, Qwiic_Adaptive_Switch_Output_BOM.csv, Qwiic_Adaptive_Switch_Output_BOM.xlsx]
2021-12-19 Updated header pin order
    [Qwiic_Adaptive_Switch_Input.brd, Qwiic_Adaptive_Switch_Input.sch, Qwiic_Adaptive_Switch_Input1.1.brd, Qwiic_Adaptive_Switch_Input1.1.sch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]
2022-04-04 Added step files
    [Qwiic_Adaptive_Switch_Input.step, Qwiic_Adaptive_Switch_Input_Assembly_RevA .step, Qwiic_Adaptive_Switch_Output.step, Qwiic_Adaptive_Switch_Output_Assembly_Rev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]
2023-04-10 Added Risk Assessment documents
    [Qwiic-Adaptive-Switch-Input-Risk-Assessment.xlsx]

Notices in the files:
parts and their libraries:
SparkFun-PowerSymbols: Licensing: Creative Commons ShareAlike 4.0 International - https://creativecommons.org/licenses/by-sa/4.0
